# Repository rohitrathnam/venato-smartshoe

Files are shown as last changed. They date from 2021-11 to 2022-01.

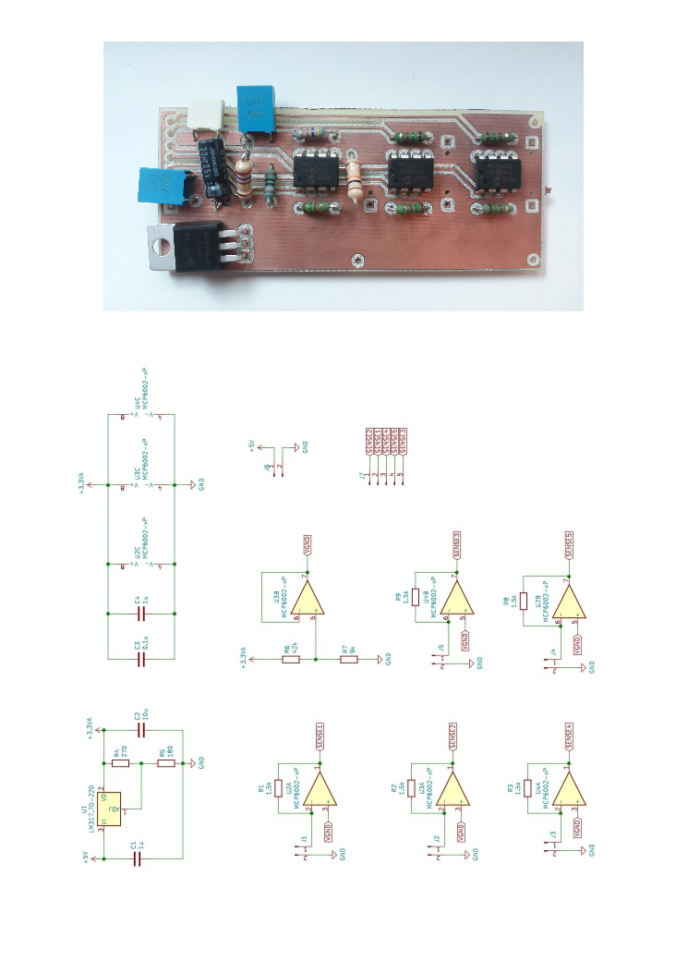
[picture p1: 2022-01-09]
media/schematicpcb.png

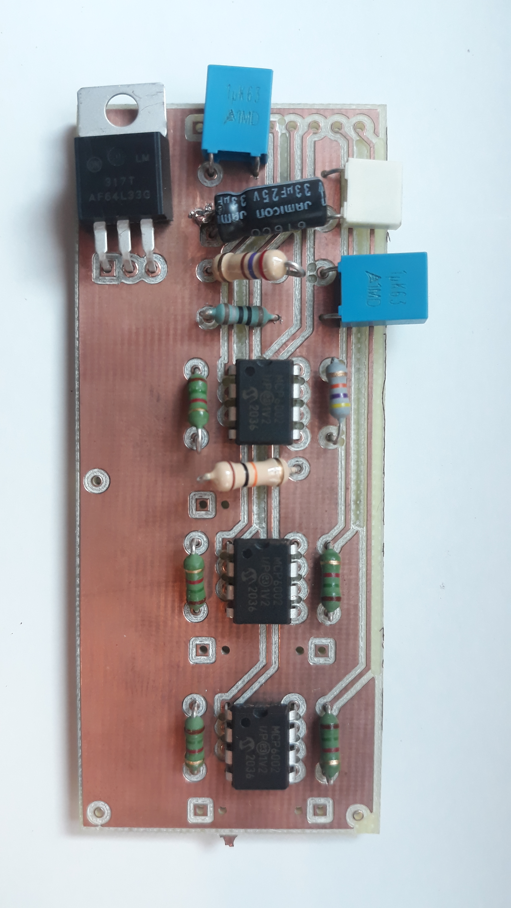
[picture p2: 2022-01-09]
media/20211012_102447.jpg

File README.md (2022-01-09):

# Venato Smart Shoe
HL2032 team project to create a smart shoe that measures pressure distribution and gait parameters of the feet. 

## Lean Canvas

### Problem
1. Conditioning coach: As a conditioning coach, I want to have deep analysis of foot pressure during exercises such as squats or deadlift.  Plus, I want to perform kinetic tests that requires Force plates and labs, anytime. maybe after a workout. Besides, jumping parameters, such as impact time, landing forces etc are really important in order to prevent injuries for me.
1. As a fitness user, I want track my fitness through step counts and visualise on my devices
1. As a senior care provider, I want the device to record foot pressure distributions to track posture and joint health
2. As a physiotherapist, I want to visualise the different gait parameters to assess posture and monitor corrections
3. As a user I want the device to be wireless for ease of use

### Customer-segment
1. Fitness tracking
1. Gait / posture correction
1. Senior care
2. Rehabilitation

### Unique-Value-Proposition
**Single**, _clear_, `compelling` message that states why you are different and worth buying
- Compatible with any shoe
- Foot pressure distribution, stride duration, step duration, swing and stance duration, gait cadence, gait frequency, double support duration, velocity
- Supports outdoor tracking
- Low cost alternative
- Product ecosystem - mobile / desktop / browser to visualise data

### Solution
- Create a bluetooth enabled sole with contact force, gyros and IMU which can be slipped any shoe

### Channels
- Retailers (online/specialized stores/mainstream stores)
- Physiotherapist
- Social media
- Point of sale

### Cost-Structure
- Customer aquisition costs
- Distribution costs
- Hosting
- People
- Parts

### Revenue-Stream
- Unit sales 
- Subscription for personalised analytics
- Strategic partnerships with training / rehab centres

### Key-Metrics
- Sensitivity, accuracy, specificity, repeatability, reliability of measurements
- Response time 
- Battery life 
- Position of pressure points
- Another key activity to measure

### Unfair-advantage
- New intellectual property
- Currently no competition

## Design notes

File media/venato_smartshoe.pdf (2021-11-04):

## Smart Shoe

Medical Engineering, Project Course Hardi Hamshin, Federica Carmen Maruccio, Mahyar Mehr, Rohit Nareshkumar, Phuong Huy Nguyen. October 2021

Abstract

In the area of digital health, there is a huge demand of collecting data about an individual’s gait deviations, such as in pathological subjects like parkinsonians, hemiplegics or choreiforms as well as in elderly people. Gait analysis using an instrumented treadmill, which is the commonly used method produces a noisy signal due to the friction in a belt [1]. Considering this, a smart shoe could be a solution for a more reliable gait analysis. Equipped with force sensitive resistors and IMUs, it can be used to keep track of the foot pressure distribution and several gait parameters.
Introduction

Smart wearable technologies, with potential to gather information through sensors [2], has shown to have the possibility to improve one’s life either in a reactive way or a preventive way [3]. There is a huge demand of collecting data about an individual’s gait deviations, for instance in pathological subjects like parkinsonians, hemiplegics or choreiforms as well as in elderly people to check their posture or joint health. Furthermore, the extraction of pressure and gait parameters can be exploited also by fitness users who want to track their training sessions through steps count and visualize their progress on mobile devices.
The concept of a smart shoe for reliable gait analysis has already been implemented with several different methods, one approach is through data gathering from pressure sensors, accelerometers and gyroscopes [4].
As such, the purpose of this project is to create a Bluetooth enabled sole with force sensitive resistors and IMUs which can be used to keep track of the foot pressure distribution and several gait parameters.
Design

The Smart Shoe is a wireless, wearable and lowcost monitoring system that enables a real-time gait analysis, transmission and logging of the acquired data to a MATLAB application. It comprises of an instrumented insole inside the patient’s shoe and a shoe attachment containing the circuit board positioned on the ankle. The insole and shoe module contains:

- a generic shoe insole compatible with any shoe;
- five Force Sensitive Resistors (FSR04CE-ND) that measure continuous pressure;
- two 9-axis IMU (LSM9DS1) containing a 3D magnetometer, a 3D accelerometer and a 3D gyroscope with I2C and SPI for the analysis of the kinematic motion of the foot;
- an Arduino NANO 33 BLE with the nRF52840 microcontroller and a Bluetooth Low Energy connection;

A block diagram of the system architecture is shown in figure 1.

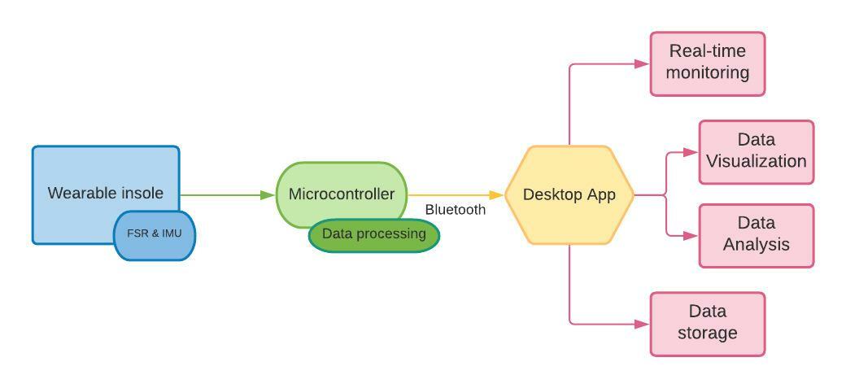
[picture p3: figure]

Figure 1: System architecture and data processes

Hardware implementation: The force sensors have a change in resistance based on the applied force. The hardware implementation to measure this consists of an opamp circuit in inverting configuration to measure the current through the resistor as a voltage. The output of the opamps are connected to the ADC pins, and both of the IMUs over the I2C bus. A circuit board was milled to contain the analog circuit, shown in figure 5.
Software implementation: The embedded software is developed using ARM mBed. The data is filtered and aggregated in a packet, sent over BLE to a computer. A MATLAB script is used to log the data and post process foot pressure distribution and gait parameters.

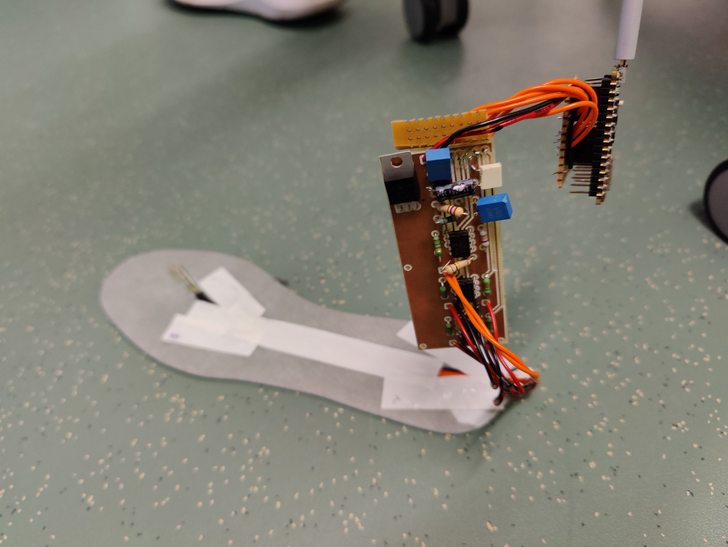
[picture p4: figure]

Figure 2: Prototype

Evaluation

IMU data processing: Firstly, we compensate the sensor inaccuracies such as zero level offset, scaling, and misalignment in three axes of the accelerometer and gyroscope contained in the two IMUs. Stančin e Tomažič refinement [5] is used for this purpose. The process involves rotating the real axis of the IMU into the axis of the leg vector.
Once the IMU has been calibrated, initial and final foot contacts (IC and F C) are estimated using Trojanello method [6]. Time intervals of trusted swing (TSW ) and of trusted stance (TST ) are identified and the remaining time intervals are used as IC and F C search intervals (TIC and

TF C).

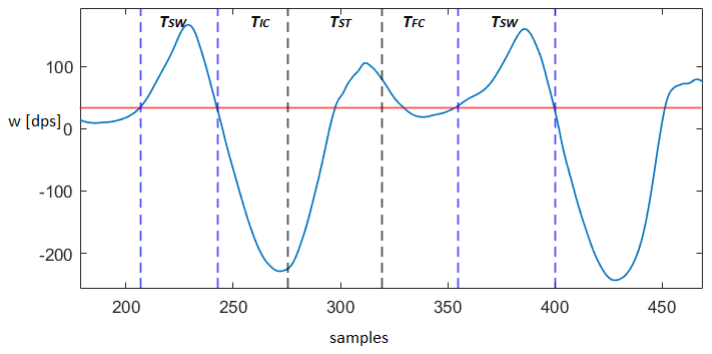
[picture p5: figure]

Figure 3: IC and FC estimation

Once the ICs and F Cs are identified, Stride Time, Step Time, Swing Time and Stance Time are calculated per gait cycle. Furthermore, spatial parameters could be estimated using a method named Trusted Events and Acceleration

Direct and Reverse Integration along the direction of Progression (T EADRIP) [7].
Pressure data processing The force sensor produces a response curve resulting in a drop in resistance proportional to the force applied. The sensor has an accuracy of about 5%, and so cannot be used for absolute measurements. However, the relative forces give us the weight distribution between heel and foot as well as the transverse distribution. Studies have shown that aging related anatomical effects on the foot can be diagnosed using the pressure distribution during the various gait phases [8]. The forces sensors also help in segmenting the gait into the different phases - this timing information is used to verify the segmentation of IMU data. The differences in amplitude of force graphs are used to detect femoral anteversion, internal tibial torsion, and matetarsus adductus (in-toe and out-toe).

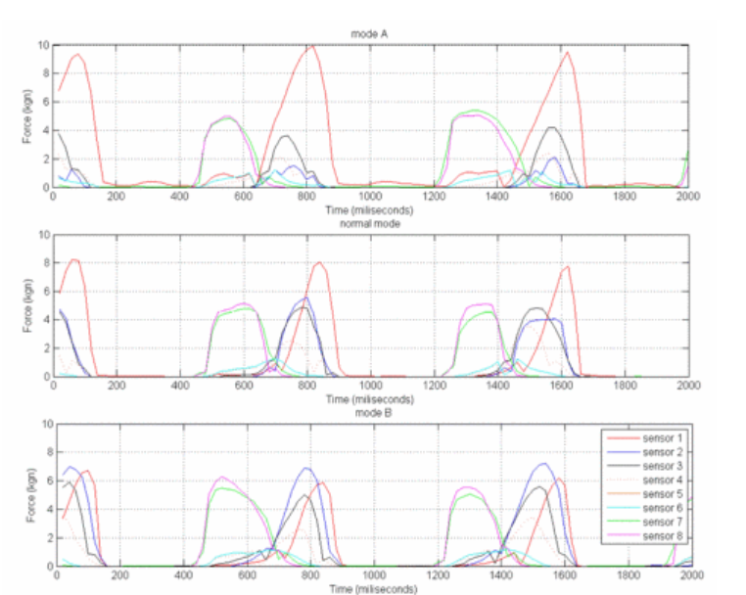
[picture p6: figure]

Figure 4: Force sensor response for in-toe and out-toe (not our data)

Conclusion

In conclusion, we outlined the considerations for the design and fabrication of a smart shoe sole to analyse gait parameters for monitoring, diagnosis and rehabilitation. The sole offers low cost and portable alternative to visual analysis or the use of pressure plates while circumventing some of their drawbacks. Beyond m-health, this device also has applications in fitness tracking, gait correction, and geriatric care and monitoring.

## References

[1] Brian K Higginson. “Methods of running gait analysis”. In: Current sports medicine reports 8.3 (2009), pp. 136–141.
[2] Eskofier B. M.; Lee S. I.; Baron M.; Simon A.; Martindale C. F.; Gaßner H.; Klucken
J. “An overview of smart shoes in the internet of health things: gait and mobility assessment in health promotion and disease monitoring”. In: Applied Sciences 7(10) (2017),
p. 986.
[3] Glaros C.; Fotiadis D. I. “Wearable devices in healthcare. In Intelligent paradigms for healthcare enterprises”. In: Springer (2005), pp. 237–264.
[4] Sunarya U.; Sun Hariyani Y.; Cho T.; Roh J.; Hyeong J.; Sohn I.; Park C. “Feature analysis of smart shoe sensors for classification of gait patterns”. In: Sensors 20(21) (2020), p. 6253.
[5] Sara Stančin; Sašo Tomažič. “Time- and Computation-Efficient Calibration of MEMS

3D Accelerometers and Gyroscopes”. In: Sensors 14 (2014), pp. 14885–14915.

[6] Diana Trojaniello; Andrea Cereatti; Gabriele Paolini; Andrea Ravaschio; Ugo Della Croce. “Temporal gait parameters determination from shank-worn MIMU signals recorded during healthy and pathological gait”. In: (2013).
[7] Matilde Bertoli; Andrea Cereatti; Diana Trojaniello; Laura Avanzino; Elisa Pelosin; Silvia Del Din; Lynn Rochester; Pieter Ginis; Esther M. J. Bekkers; Anat Mirelman; Jeffrey M. Hausdorff; Ugo Della Croce. “Estimation of spatio-temporal parameters of gait from magneto-inertial measurement units: Multicenter validation among Parkinson, mildly cognitively impaired and healthy older adults”. In: BioMedical Engineering OnLine (2018).
[8] Mary Josephine Hessert et al. “Foot pressure distribution during walking in young and old adults”. In: BMC geriatrics 5.1 (2005), pp. 1– 8.

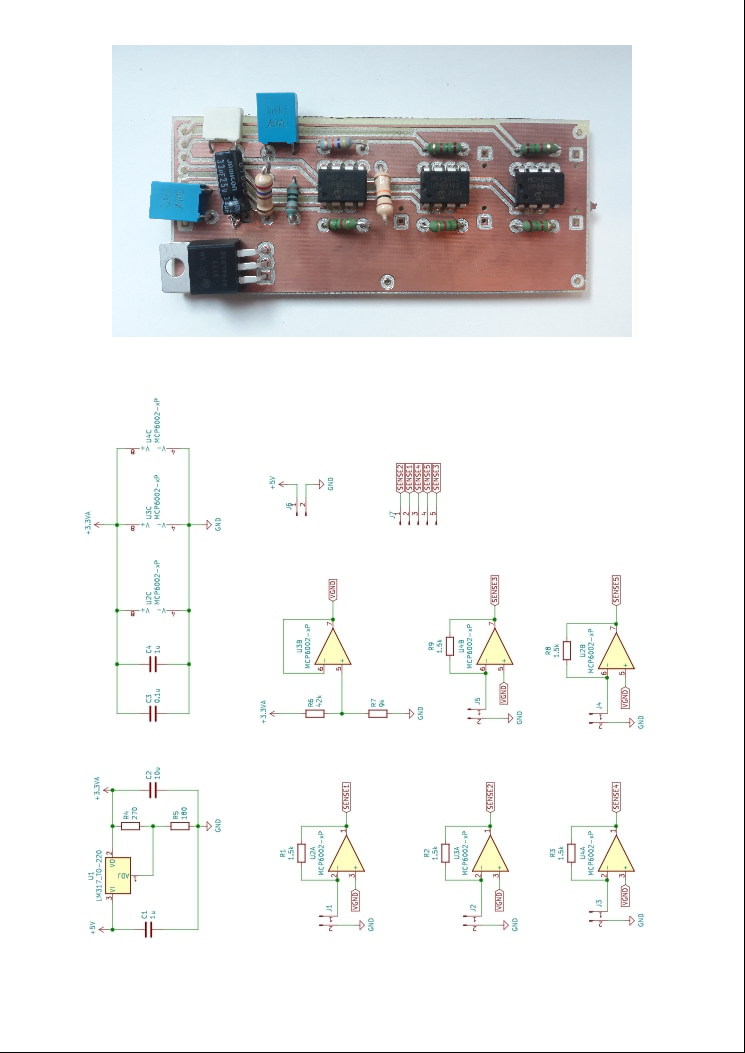
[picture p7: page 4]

Figure 5: Schematic and circuit board

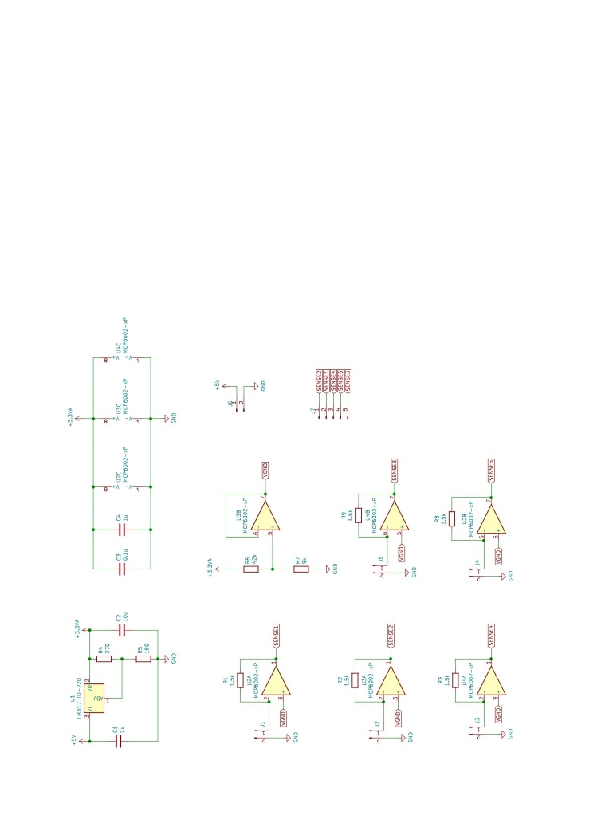
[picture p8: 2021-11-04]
hardware/v2/schematic.jpg

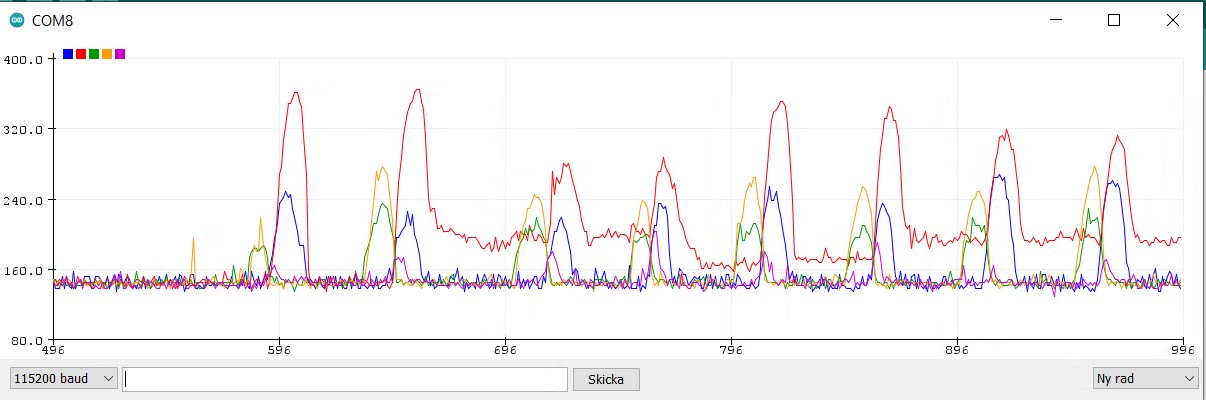
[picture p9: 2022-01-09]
media/Out_toe.jpg

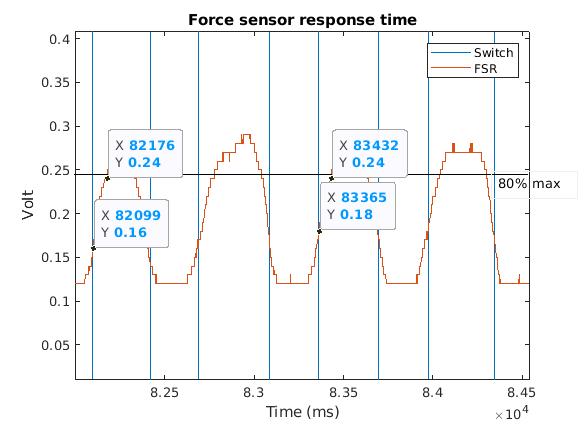
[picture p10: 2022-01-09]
media/fsrtime.jpg

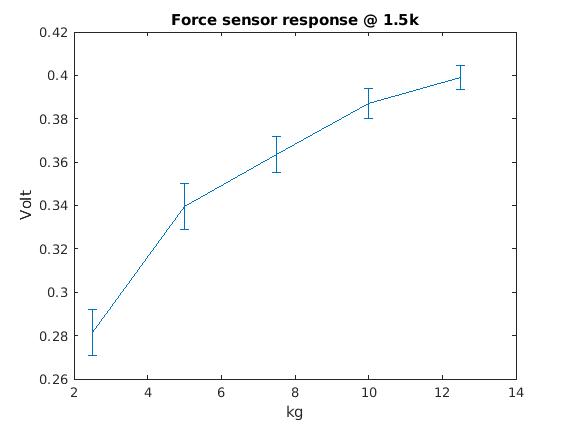
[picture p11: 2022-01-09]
media/volt-vs-weight-1k5.jpg

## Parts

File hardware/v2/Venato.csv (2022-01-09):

Reference | Quantity | Value | Footprint
C2 | 2 | 10u | Capacitor_SMD:C_0805_2012Metric_Pad1.18x1.45mm_HandSolder
C3 | 2 | 0.1u | Capacitor_SMD:C_0805_2012Metric_Pad1.18x1.45mm_HandSolder
C1 C4 | 5 | 1u | Capacitor_SMD:C_0805_2012Metric_Pad1.18x1.45mm_HandSolder
R1 R2 R3 R8 R9 | 10 | 1.5k | Resistor_SMD:R_0805_2012Metric_Pad1.20x1.40mm_HandSolder
R4 | 2 | 270R | Resistor_SMD:R_0805_2012Metric_Pad1.20x1.40mm_HandSolder
R5 | 2 | 180R | Resistor_SMD:R_0805_2012Metric_Pad1.20x1.40mm_HandSolder
R6 | 2 | 42k | Resistor_SMD:R_0805_2012Metric_Pad1.20x1.40mm_HandSolder
R7 | 2 | 9k | Resistor_SMD:R_0805_2012Metric_Pad1.20x1.40mm_HandSolder
U2 U3 U4 | 4 | MCP6002-xP | Package_SO:MSOP-8_3x3mm_P0.65mm
 | 6 | FSR04B

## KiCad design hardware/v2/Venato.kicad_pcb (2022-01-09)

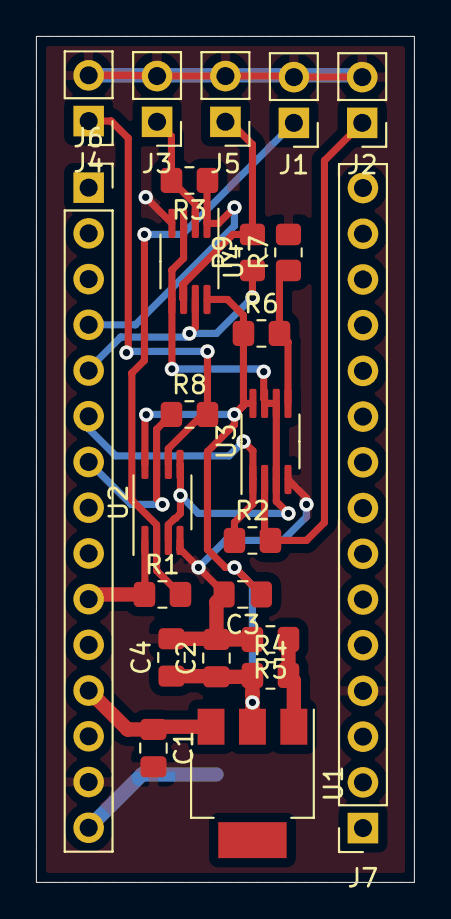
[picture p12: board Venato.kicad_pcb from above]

Board: 2 copper layers, 21.0 x 47.0 mm, 25 parts (1 on the bottom side), 17 nets.

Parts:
C1, C4: 1u; C_0805_2012Metric_Pad1.18x1.45mm_HandSolder
C2: 10u; C_0805_2012Metric_Pad1.18x1.45mm_HandSolder
C3: 0.1u; C_0805_2012Metric_Pad1.18x1.45mm_HandSolder
J1, J2, J3, J4, J5: Conn_01x02_Male; PinHeader_1x02_P2.54mm_Vertical
J6, J7: Conn_01x15_Female; PinSocket_1x15_P2.54mm_Vertical
J8: Conn_01x02_Male; JST_PH_B2B-PH-SM4-TB_1x02-1MP_P2.00mm_Vertical
R1, R2, R3, R8, R9: 1.5k; R_0805_2012Metric_Pad1.20x1.40mm_HandSolder
R4: 270; R_0805_2012Metric_Pad1.20x1.40mm_HandSolder
R5: 180; R_0805_2012Metric_Pad1.20x1.40mm_HandSolder
R6: 42k; R_0805_2012Metric_Pad1.20x1.40mm_HandSolder
R7: 9k; R_0805_2012Metric_Pad1.20x1.40mm_HandSolder
U1: LM317_TO-220; SOT-223
U2, U3, U4: MCP6002-xP; MSOP-8_3x3mm_P0.65mm

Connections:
+3.3VA: C2.1, C3.1, C4.1, R4.1, R6.1, U1.2, U2.8, U3.8, U4.8
+5V: C1.1, J6.12, U1.3
GND: C1.2, C2.2, C3.2, C4.2, J1.2, J2.2, J3.2, J4.2, J5.2, J6.14, J7.4, J8.2, R5.2, R7.2, U2.4, U3.4, U4.4
unnamed: J1.1, R1.2, U2.2
unnamed: J2.1, R2.2, U3.2
unnamed: J3.1, R3.2, U4.2
unnamed: J4.1, R8.2, U2.6
unnamed: J5.1, R9.2, U4.6
unnamed: R4.2, R5.1, U1.1
unnamed: R6.2, R7.1, U3.5
SENSE1: J6.10, R1.1, U2.1
SENSE2: J6.6, R2.1, U3.1
SENSE3: J6.5, R9.1, U4.7
SENSE4: J6.4, R3.1, U4.1
SENSE5: J6.7, R8.1, U2.7
VGND: U2.3, U2.5, U3.3, U3.6, U3.7, U4.3, U4.5
VIN: J6.15, J8.1

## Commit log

2021-09-27 Opamp schematic
    [Venato.kicad_pcb, Venato.sch]
2021-09-30 Added PCB
    DRC ok, need to generate gerbers
    [Venato.sch]
2021-11-17 v2 pcb init
    [Venato.csv, Venato.kicad_pcb, Venato.sch]
2021-11-24 1mm traces and fix resistor
    [Venato.kicad_pcb, Venato.sch]
2022-01-02 updated arduino code
    [Venato-B_Cu.gbr, Venato-Edge_Cuts.gbr, Venato-F_Cu.gbr, Venato-NPTH.drl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]
2022-01-07 v2 pcb done
    [Venato.kicad_pcb, Venato.sch]
2022-01-09 removing files due to conflict
    [Venato-B_Cu.gbr, Venato-Edge_Cuts.gbr, Venato-F_Cu.gbr, Venato-NPTH.drl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]
2022-01-09 Logs and Media
    [Testing.csv, Walking_intoe.xlsx, intoefsr.xlsx, jump.xlsx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]
2022-01-09 Calibration code
    Matlab code for IMU calibration
